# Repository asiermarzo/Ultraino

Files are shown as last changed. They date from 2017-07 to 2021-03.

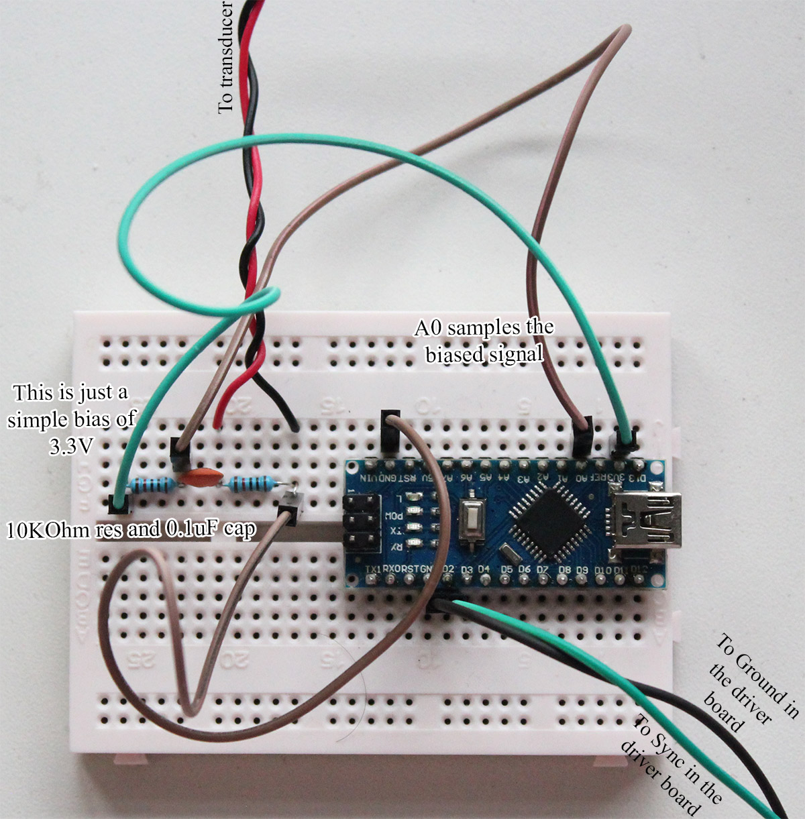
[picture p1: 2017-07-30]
Arduino phase detector/schematics.jpg

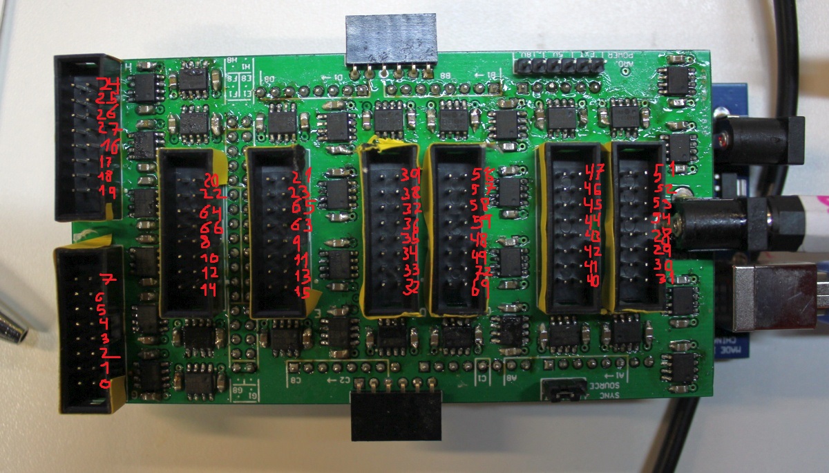
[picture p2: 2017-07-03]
DriverBoards/ArduinoMega64/driver board/ArduinoMEGA64 pin layout.JPG

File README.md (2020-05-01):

# Ultraino
Acoustic Field simulation for phased-array controllers. The content of the folders is as follows:
- AcousticField3D. The simulator that runs on the PC and can control the driver boards
- Arduino MEGA 64 driver board code. Source code that goes in the Arduino Mega 64-channel driver board.
- DriverNano16. Source code for making an Arduino Nano a 16-channel driver board.
- Arduino phase detector. Code that goes in an Arduino Nano to serve as a tool to assign the channels.
- arrays. Bases for example arrays.
- driver board. BOM and PCB files for the driver board.

# How to Run the Software
* Download the source as a zip file or checkout the repository.

* Be sure that you have installed JDK 11 https://www.oracle.com/java/technologies/javase-jdk11-downloads.html
* Install Netbeans Integrated Development Environment (you can also use Eclipse if you want). The Java SE pack is enough https://netbeans.org/downloads/

* Import the Source code in Netbeans. Run Netbeans, File->Open Project, Select the folder with the sourcecode.
* Click Run. You can click Run->Run project. It will take some time the first time since it needs to compile the sourcecode.

# Install Arduino Software
* Install the Arduino IDE https://www.arduino.cc/en/Main/Software
* Run the Arduino IDE and connect the Arduino Board to your computer.
* In Tools->Board select Arduino/Genuino Mega or Mega 2560. In Tools->Ports select the port for your Arduino. You may need to install the drivers for your Arduino Board (specially if it is not a branded one). For the chip CH340 http://sparks.gogo.co.nz/ch340.html
* In the public interface of Program Files (x86)\Arduino\hardware\arduino\avr\cores\arduino\HardwareSerial.h
add the following inline functions
inline bool _dataAvailable() {return _rx_buffer_head != _rx_buffer_tail; }
inline byte _peekData() { return _rx_buffer[_rx_buffer_tail]; }
inline void _discardByte() { _rx_buffer_tail = (rx_buffer_index_t)(_rx_buffer_tail + 1) % SERIAL_RX_BUFFER_SIZE; } 
* Click the Icon for Upload

# Install the Channel detector (tiny device used to assign channels semiautomatically)
* There is a schematic in the folder
* Install the software in Arduino Nano

# How to Assemble and example Applications
Paper: http://ieeexplore.ieee.org/document/8094247/
Instructables: https://www.instructables.com/id/Ultrasonic-array/
Video: https://youtu.be/h0Mh0bIv9Fk

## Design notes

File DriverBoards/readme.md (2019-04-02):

# Driver Boards

These are the files required to build the electronics.

## SonicSurface-256
This is a 256 channel board based on the Intel Cycloine IV FPGA. It has integrated ultrasonic transducers and a phase resolution of pi/16.

## ArduinoMega-64
This is a 64 channel board based on the Arduino Mega. It has a phase resolution of pi/5

# Links to papers & instructables

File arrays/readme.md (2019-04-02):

# Files for building the ultrasonic arrays

## 3D printing files (.stl)
These are provided as stl files which can be opened by probably all 3D printer software.

## Laser cutting files (.ai)
These are provided in Adobe Illustrator format (.ai). Inkscape is recommneded to open these or Adobe Illustrator CS2 is now avaialble as free software although its very old.

## Simulation Files (.xml.gz)
The simulation files are gun-zipped xml files and have the extension .xml.gz - they are used in the Acoustic Field Simulator software which is also in this repository. 

# Parts List
* 20-core ribbon cable [from UK Farnell](http://uk.farnell.com/3m/3302-20/ribbon-cable-20core-28awg-per/dp/1207420)
* 3-way pcb connector
  * uk rs-components 506-7014
* female molex connector
  * uk rs-components 323-7873
* 40khz 1cm diameter transducers
 * MURATA: uk rs-components 237-0799
* The murata transducers are a little bit pricey so here are some alternatives:
  * Manorshi Black 10mm - 0.34$ - MSO-P1040H07T [from alibaba](https://manorshi.en.alibaba.com)
  * Ningbo Black 10mm - 0.38$ - 'dog repeller' [from alibaba](FBULS1007P-T https://bestgroup.en.alibaba.com/product/987365133-800848321/dog_repeller_ultrasonic_transducer_40khz_black_plastic_ultrasonic_sensor_ultrasonic_depth_sensor.html)

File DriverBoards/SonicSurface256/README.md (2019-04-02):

# SonicSurface-256

The build instructions will be added here once we get around to it.

## Build Of Materials (BOM)

## Phase Calibration & board rotation

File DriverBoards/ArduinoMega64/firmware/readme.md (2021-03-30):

DriverMEGA is the normal code. It can upload up to 32 patterns and then a script is sent that indicates how many periods each pattern should be played.
DriverMEGAAnim is designed to upload 32 patterns at the same time and then send only one byte for the desired pattern
DriverMEGAStatic is designed for operating without a computer since the 32 patterns are predefined and it is possible to cycle through them by external buttons. These patterns can be generated with the simulator.

Please do not forget to add in the public interface of HardwareSerial the following inlines: 

inline bool _dataAvailable() {return _rx_buffer_head != _rx_buffer_tail; }
inline byte _peekData() { return _rx_buffer[_rx_buffer_tail]; }
inline void _discardByte() { _rx_buffer_tail = (rx_buffer_index_t)(_rx_buffer_tail + 1) % SERIAL_RX_BUFFER_SIZE; }

They are located at Program Files (x86)\Arduino\hardware\arduino\avr\cores\arduino\HardwareSerial.h
For MAC the path may be "HD -> Applications -> Arduino -> Contents -> Java -> hardware -> arduino -> avr -> cores -> arduino"

Just after the line "public:" is fine.

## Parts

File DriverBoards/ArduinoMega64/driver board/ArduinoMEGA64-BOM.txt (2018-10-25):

62mm by 115mm 
4 layers

32x TC4427A SMD / or MIC4127 for more voltage
	uk rs-components 889-5409
32x caps ceramic SMD 0805 0.1uf above 25V
	uk rs-components 264-4416
32x caps ceramic SMD 0805 4.7uf above 25V
	uk rs-components 820-2778
8x MOLEX male 16way connectors
	http://uk.farnell.com/amphenol/t821116a1s100ceu/header-vertical-2-54mm-16way/dp/2215308
	http://uk.farnell.com/molex/70246-1604/header-shrouded-16way/dp/1392536
1x DC barrel
	http://amzn.eu/7HL7QDk
Headers pins
	http://amzn.eu/bA4vE4o
90deg angle pins female and female 6-way
	http://amzn.eu/a4pMjJ7
jumper
	http://amzn.eu/7xdVyIM

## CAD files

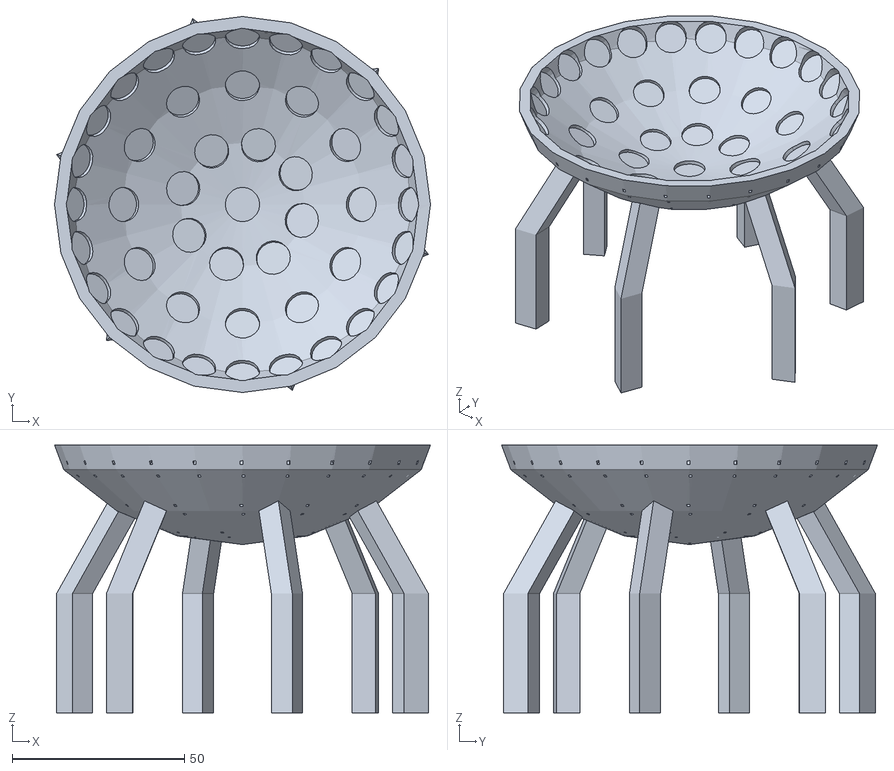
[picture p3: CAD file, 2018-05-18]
arrays/sphericalCap48.STL
109.3 x 109.3 x 77.9

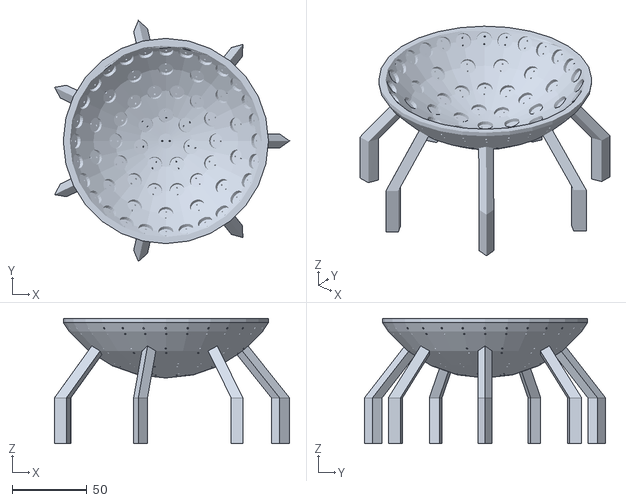
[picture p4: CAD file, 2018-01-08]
arrays/sphericalCap64.STL
157.7 x 161.7 x 83.9

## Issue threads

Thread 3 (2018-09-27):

asiermarzo/Ultraino #3: DriverNano16

vrossbach, 2018-09-27:
I am trying to upload the code for DriverNano16 in the Arduino Uno and this error messages appear:

'class HardwareSerial' has no member named '_dataAvailable'
'class HardwareSerial' has no member named '_peekData'

I tried to put the functions Serial.available() and Serial.peek() but then there is a error to compile to Arduino Uno board. Is there a different code for Arduino Uno or the code was written in another version?

asiermarzo, 2018-09-27:
Try the instructions on https://github.com/asiermarzo/Ultraino/blob/master/Arduino%20MEGA%2064%20driver%20board%20code/readme.txt

Best

vrossbach, 2018-09-27:
Hi, 

now I got, I had not pasted the code in the correct public position.

Thank you!

closed 2019-03-29 by asiermarzo

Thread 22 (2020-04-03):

asiermarzo/Ultraino #22: Noise on signal when doing semi-manual pin assignment, software frozen

littlejacinthe, 2020-04-03:
Hello, 

When doing the semi-manual pin assignment following the steps of your video, we noticed that :
- The Ultraino software stops working at : 
Transducer Assignment menu > Connect (Arduino Nano is connected correctly) > Start > Check.  Once we click on the 'check' command there is no output when it should show numbers for Selected, Pin, Amplitude, Phase. After that the software is completely frozen and we have to restart it. 
It probably is because the software does not detect the signal coming from the transducers correctly, as when we checked it with the oscilloscope : 
- There is noise provided by the transducer used to check the signal when it's connected to wires. We tried different wires but there was always noise, which doesn't happen when the transducer is directly connected to the probe of the oscilloscope.

We used all materials recommended as well the codes provided during this experiment. 
Our driver is an Arduino MEGA, and we are working on an 8x8 flat array. 
You can see how we proceeded on [this video](https://youtu.be/fm1WUwtMGUc). It shows more precisely the problem that we're having. 

Would you have any idea why is this happening and how to solve the problem ?

Thank you

asiermarzo, 2020-04-08:
Hi,
Very good work with the video and with the hardware. Ultraino started as research and still needs a lot of brushing up.

a) Have you installed the phase-detector sketch in the arduino that is used to detect the pins?
b) when you connect the driverboard and the phase-detector have you identified which COM port is which?
c) be sure to connect the main program to the board and the connect of the assignments to the phase detector.

In any case, I will try to add more debug messages and avoid the software from hanging.

Best,
Asier.

littlejacinthe, 2020-04-10:
Hello, 

a) we installed the phase-detector sketch using the same materials 
[image]
b) and c) We made the mistake of connecting the wrong ports before but corrected it and then this noise problem came up. 

We are going to order brand new materials for the phase detector as the ones we've been using are not and there might be a default there. 

Thanks for your reply !

littlejacinthe, 2020-04-16:
Hello, 

After changing the hardware of the arduino phase detector, we still got the same error. 

I noticed when connecting the Arduino Nano that we have to use the old bootloader for ATMega 328P otherwise it doesn't upload the code. It seems like the bootloader was updated in 2018. Could it be that you used the new bootloader ? 

Also on line 34 of the phase detector code, the line should print the samples array. When the board is connected to the simulation software it says the port is busy, and when the board is not connected to the simulation software (with only the Mega board sending the signal to the transducers) the monitor is empty. Is that normal ?

Thanks

asiermarzo, 2020-09-13:
It is not possible to have the phase detector working and the serial monitor connected to it. Have you selected the transducers in the order that you want them tested and then pressed the button Order? Otherwise, all of them may have order 0 and cause problems. Best. I know the phase assignment works like shit, I need to brush it up asap.

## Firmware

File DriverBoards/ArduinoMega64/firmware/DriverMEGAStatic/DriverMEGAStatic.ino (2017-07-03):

#include <avr/sleep.h>
#include <avr/power.h>

#define N_PATTERNS 8

#define N_PORTS 10
#define N_DIVS 10

//ports A C L B K F H D G J

#define COMMAND_SWITCH 0b00000000
#define COMMAND_DURATION 0b00110000
#define MASK_DURATION 0b00111111
#define COMMAND_COMMITDURATIONS 0b00010000

#define WAIT(a) __asm__ __volatile__ ("nop")
#define OUTPUT_WAVE(pointer, d)  PORTA = pointer[d*N_PORTS + 0]; PORTC = pointer[d*N_PORTS + 1]; PORTL = pointer[d*N_PORTS + 2]; PORTB = pointer[d*N_PORTS + 3]; PORTK = pointer[d*N_PORTS + 4]; PORTF = pointer[d*N_PORTS + 5]; PORTH = pointer[d*N_PORTS + 6];  PORTD = pointer[d*N_PORTS + 7]; PORTG = pointer[d*N_PORTS + 8]; PORTJ = pointer[d*N_PORTS + 9]

static byte bufferA[N_PATTERNS * N_DIVS * N_PORTS];
static byte bufferB[N_PATTERNS * N_DIVS * N_PORTS];

static byte animation[100] = {0x38,0xa8,0xb4,0x3,0x2,0xfc,0x43,0xc,0x4,0x0,0x3d,0xaa,0xac,0x3,0x2,0xfc,0x43,0xc,0x7,0x0,0x5,0x3,0x8,0xe4,0x38,0x6d,0x19,0xb,0x3,0x1,0x7,0x43,0xa,0xe4,0x38,0x6d,0x19,0x8b,0x3,0x1,0x7,0x43,0xa,0xe4,0x38,0x1,0x18,0x83,0x3,0x1,0x7,0x57,0x4b,0xfc,0x3d,0x3,0x38,0x83,0x23,0x1,0x2,0x55,0x53,0xfc,0x3d,0x3,0x38,0x83,0x20,0x1,0x3a,0xfc,0xf7,0x1b,0x7,0x92,0x62,0x84,0x24,0x0,0x38,0xbc,0xf5,0x1b,0x7,0x92,0x62,0x4,0x24,0x0,0x38,0xbc,0xf5,0x1b,0x7,0xfe,0x63,0xc,0x24,0x0};

void setup()
{
  //set as output ports A C L B K F H D G J
  DDRA = DDRC = DDRL = DDRB = DDRK = DDRF = DDRH = DDRD = DDRG = DDRJ = 0xFF;
  //low signal on all of them
  PORTA = PORTC = PORTL = PORTB = PORTK = PORTF = PORTH = PORTD = PORTG = PORTJ = 0x00;

  //clear the buffers
  for (int i = 0; i < (N_PATTERNS * N_DIVS * N_PORTS); ++i) {
    bufferA[i] = bufferB[i] = 0;
  }

//initial pattern
/*
  for (int i = 0; i < (N_PORTS*N_DIVS/2); ++i){
     bufferA[i] = 0xFF;
     //bufferA[i] = bufferB[i] = animation[i];
  }
  */
 
   for (int i = 0; i < 100; ++i){
      bufferA[i] =  animation[i];
   }

 for (int i = 0; i < 100; ++i){
       bufferB[i] =  animation[i];
   }

  //a patterns of 01s at pin 22, for debuging and adjusting times
 /*
  for(int i = 0; i < N_DIVS; ++i){
    if (i % 2 == 0){
      bufferA[i * N_PORTS] |= 0b00001000;
    }else{
      bufferA[i * N_PORTS] &= 0b11110111;
    }
  }
 */
  
  // generate a sync signal of 40khz in pin 2
  pinMode (2, OUTPUT);
  noInterrupts();           // disable all interrupts
  TCCR3A = bit (WGM10) | bit (WGM11) | bit (COM1B1); // fast PWM, clear OC1B on compare
  TCCR3B = bit (WGM12) | bit (WGM13) | bit (CS10);   // fast PWM, no prescaler
  OCR3A =  (F_CPU / 40000L) - 5; //should only be -1 but fine tunning with the scope determined that -5 gave 40kHz almost exactly
  OCR3B = (F_CPU / 40000L) / 2;
  interrupts();             // enable all interrupts

  //sync in signal at pin 3
  pinMode(3, INPUT_PULLUP); //please connect pin3 to pin 2


  // disable everything that we do not need
  ADCSRA = 0;  // ADC
  power_adc_disable ();
  power_spi_disable();
  power_twi_disable();
  power_timer0_disable();
  power_usart1_disable();
  power_usart2_disable();
  power_usart3_disable();
  //power_usart0_disable();

  Serial.begin(115200);

  byte bReceived = 0;
  bool byteReady = false;
  bool isSwitch = false;
  bool isPatternForMe = false;
  bool isDuration = false;
  bool isCommitDurations = false;
  byte nextMsg = 0;
  int writtingIndex = 0;

  bool emittingA = true;
  byte* emittingPointerH = & bufferA[0];
  byte* emittingPointerL = & bufferA[N_PORTS * N_DIVS / 2];
  byte* emittingPointerZeroH = & bufferA[0];
  byte* emittingPointerZeroL = & bufferA[N_PORTS * N_DIVS / 2];
  byte* readingPointerH = & bufferB[0];
  byte* readingPointerL = & bufferB[N_PORTS * N_DIVS / 2];

  byte durations[N_PATTERNS];
  byte durationsBuffer[N_PATTERNS];
  for(int i = 0; i < N_PATTERNS; ++i){
    durations[i] = durationsBuffer[i] = 0;
  }
  durations[0] = durationsBuffer[0] = 1;

  byte currentPattern = 0;
  byte currentPeriods = 0;
  byte durationsPointer = 0;
  byte currentDuration = 0;
  bool patternComplete = false;
  bool lastPattern = false;
  byte nextPattern = 0;
  byte nextDuration = 0;
  bool returnToFirstPattern = false;
LOOP:
  while (PINE & 0b00100000); //wait for pin 3 (E5 Sync In) to go low

  OUTPUT_WAVE(emittingPointerH, 0); byteReady = Serial._dataAvailable(); 
  OUTPUT_WAVE(emittingPointerH, 1); bReceived = Serial._peekData(); 
  OUTPUT_WAVE(emittingPointerH, 2); isSwitch = bReceived == COMMAND_SWITCH; isCommitDurations = bReceived == COMMAND_COMMITDURATIONS; 
  OUTPUT_WAVE(emittingPointerH, 3); isPatternForMe = (bReceived & 0b00001111) == 1; ++currentPeriods; 
  OUTPUT_WAVE(emittingPointerH, 4); nextMsg =  bReceived - 1; 
  OUTPUT_WAVE(emittingPointerL, 0); isDuration = (bReceived & MASK_DURATION) == COMMAND_DURATION; nextPattern = currentPattern + 1;
  OUTPUT_WAVE(emittingPointerL, 1); nextDuration = durations[nextPattern]; 
  OUTPUT_WAVE(emittingPointerL, 2); patternComplete = (currentPeriods == durations[currentPattern]); 
  OUTPUT_WAVE(emittingPointerL, 3); lastPattern = (currentPattern+1 == N_PATTERNS); returnToFirstPattern = nextDuration == 0;
  OUTPUT_WAVE(emittingPointerL, 4); 
  
if (patternComplete){
  currentPeriods = 0;
  ++currentPattern;
  if (lastPattern  || returnToFirstPattern){
    currentPattern = 0;
    emittingPointerH = emittingPointerZeroH;
    emittingPointerL = emittingPointerZeroL;
  }else{
    emittingPointerH += (N_DIVS * N_PORTS);
    emittingPointerL += (N_DIVS * N_PORTS);
  } 
}
  
  if (byteReady) {
    if ( isSwitch ) {
      Serial.write( COMMAND_SWITCH );
      emittingA = !emittingA;
      if (emittingA) {
        emittingPointerH = & bufferA[0];
        emittingPointerL = & bufferA[N_PORTS * N_DIVS / 2];
        readingPointerH = & bufferB[0];
        readingPointerL = & bufferB[N_PORTS * N_DIVS / 2];
      } else {
        emittingPointerH = & bufferB[0];
        emittingPointerL = & bufferB[N_PORTS * N_DIVS / 2];
        readingPointerH = & bufferA[0];
        readingPointerL = & bufferA[N_PORTS * N_DIVS / 2];
      }
      emittingPointerZeroH = emittingPointerH;
      emittingPointerZeroL = emittingPointerL;
      
      writtingIndex = 0;
      durationsPointer = 0;
    } else if ( isPatternForMe ) {
        if (writtingIndex % 2 == 0) {
          readingPointerH[writtingIndex / 2] = bReceived & 0xF0;
        } else {
          readingPointerH[writtingIndex / 2] |= (bReceived >> 4);
        }
        ++writtingIndex;
    } else if (isDuration){
        Serial.write( bReceived );
        if (durationsPointer % 4 == 0) {
          durationsBuffer[durationsPointer / 4] = bReceived & 0b11000000;
        } else {
          durationsBuffer[durationsPointer / 4] |= (bReceived & 0b11000000) >> (durationsPointer % 4 * 2);
        }
        ++durationsPointer;
    }else if (isCommitDurations){
      Serial.write( bReceived );
      for(int i = 0; i<N_PATTERNS; ++i){
        durations[i] = durationsBuffer[i];
      }
      durationsPointer = 0;
    } else {
      Serial.write( nextMsg );
    }
    Serial._discardByte();
  }

  goto LOOP;

}

void loop() {}

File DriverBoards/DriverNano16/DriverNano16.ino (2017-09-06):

#include <avr/sleep.h>
#include <avr/power.h>

#define N_PORTS 2
#define N_DIVS 16

#define COMMAND_SWITCH 0b00000000
#define COMMAND_RESET 0b00010000

#define WAIT_A(a) __asm__ __volatile__ ("nop"); __asm__ __volatile__ ("nop"); __asm__ __volatile__ ("nop");  __asm__ __volatile__ ("nop"); __asm__ __volatile__ ("nop");__asm__ __volatile__ ("nop"); __asm__ __volatile__ ("nop");__asm__ __volatile__ ("nop"); __asm__ __volatile__ ("nop");  __asm__ __volatile__ ("nop"); __asm__ __volatile__ ("nop");__asm__ __volatile__ ("nop");  __asm__ __volatile__ ("nop"); __asm__ __volatile__ ("nop"); __asm__ __volatile__ ("nop");__asm__ __volatile__ ("nop");  __asm__ __volatile__ ("nop"); __asm__ __volatile__ ("nop");  __asm__ __volatile__ ("nop"); __asm__ __volatile__ ("nop")
#define WAIT_B(a) __asm__ __volatile__ ("nop"); __asm__ __volatile__ ("nop"); __asm__ __volatile__ ("nop");  __asm__ __volatile__ ("nop"); __asm__ __volatile__ ("nop");__asm__ __volatile__ ("nop"); __asm__ __volatile__ ("nop");__asm__ __volatile__ ("nop"); __asm__ __volatile__ ("nop"); __asm__ __volatile__ ("nop"); __asm__ __volatile__ ("nop"); __asm__ __volatile__ ("nop"); __asm__ __volatile__ ("nop"); __asm__ __volatile__ ("nop"); __asm__ __volatile__ ("nop"); __asm__ __volatile__ ("nop")
#define WAIT_C(a) __asm__ __volatile__ ("nop"); __asm__ __volatile__ ("nop"); __asm__ __volatile__ ("nop");  __asm__ __volatile__ ("nop"); __asm__ __volatile__ ("nop");  __asm__ __volatile__ ("nop");  __asm__ __volatile__ ("nop"); __asm__ __volatile__ ("nop");  __asm__ __volatile__ ("nop"); __asm__ __volatile__ ("nop");  __asm__ __volatile__ ("nop");  __asm__ __volatile__ ("nop")


#define OUTPUT_WAVE(pointer, d)  PORTC = pointer[d*N_PORTS + 0]; PORTD = pointer[d*N_PORTS + 1]

static byte bufferA[N_DIVS * N_PORTS];
static byte bufferB[N_DIVS * N_PORTS];

void setup()
{
  //initialize the buffers
  for (int i = 0; i < (N_PORTS*N_DIVS); ++i){
    bufferA[i] = bufferB[0] = 0;
  }

  for (int i = 0; i < (N_PORTS*N_DIVS/2); ++i){
     bufferA[i] = 0b11111111;
  }
  
 /*
  //only for calibrating WAITs
  for(int i = 0; i < N_DIVS; ++i){
    if (i % 2 == 0){
      bufferA[i * N_PORTS] |= 0b00001000;
    }else{
      bufferA[i * N_PORTS] &= 0b11110111;
    }
  }
  */

  // generate a sync signal of 40khz in pin 10
  pinMode (10, OUTPUT);
  noInterrupts();           // disable all interrupts
  TCCR1A = bit (WGM10) | bit (WGM11) | bit (COM1B1); // fast PWM, clear OC1B on compare
  TCCR1B = bit (WGM12) | bit (WGM13) | bit (CS10);   // fast PWM, no prescaler
  OCR1A =  (F_CPU / 40000L) - 1;
  OCR1B = (F_CPU / 40000L) / 2;
  interrupts();             // enable all interrupts

  //sync in signal at pin 3
  pinMode(11, INPUT_PULLUP); //please connect pin 10 to pin 11
  

  // disable everything that we do not need 
  ADCSRA = 0;  // ADC
  power_adc_disable ();
  power_spi_disable();
  power_twi_disable();
  power_timer0_disable();
  //power_usart0_disable();

  Serial.begin(115200);

   DDRC = 0b00111111;
   DDRD = 0b11111100; 
   PORTC = 0b00000000; 
   PORTD = 0b00000000; 
   
 byte bReceived = 0;
 bool byteRead = false;
 bool isSwitch = false;
 bool isReset = false;
 bool isForMe = false;
 byte nextMsg = 0;
 int writtingIndex = 0;

 byte* emittingPointer = & bufferA[0];
 byte* readingPointer = & bufferB[0];

  LOOP:
    while(PINB & 0b00001000); //wait for pin 11 (B3) to go low 
    
    OUTPUT_WAVE(emittingPointer, 0); byteRead = Serial._dataAvailable(); WAIT_C();
    OUTPUT_WAVE(emittingPointer, 1); bReceived = Serial._peekData(); WAIT_C();
    OUTPUT_WAVE(emittingPointer, 2); isSwitch = bReceived == COMMAND_SWITCH; WAIT_B();
    OUTPUT_WAVE(emittingPointer, 3); isReset = bReceived == COMMAND_RESET; WAIT_B();
    OUTPUT_WAVE(emittingPointer, 4); isForMe = (bReceived & 0b00001111) == 1; WAIT_B(); 
    OUTPUT_WAVE(emittingPointer, 5); nextMsg =  bReceived - 1; WAIT_B();
    OUTPUT_WAVE(emittingPointer, 6); WAIT_A();
    OUTPUT_WAVE(emittingPointer, 7); WAIT_A();
    OUTPUT_WAVE(emittingPointer, 8); WAIT_A();
    OUTPUT_WAVE(emittingPointer, 9); WAIT_A();
    OUTPUT_WAVE(emittingPointer, 10); WAIT_A();
    OUTPUT_WAVE(emittingPointer, 11); WAIT_A();
    OUTPUT_WAVE(emittingPointer, 12); WAIT_A();
    OUTPUT_WAVE(emittingPointer, 13); WAIT_A();
    OUTPUT_WAVE(emittingPointer, 14); WAIT_A();
    OUTPUT_WAVE(emittingPointer, 15);

    if (byteRead){
        if ( isSwitch ){
          Serial.write( COMMAND_SWITCH );
          byte* tmpPointer = emittingPointer;
          emittingPointer = readingPointer;
          readingPointer = tmpPointer;
          
          writtingIndex = 0;
        }else if ( isReset ){
          Serial.write( COMMAND_RESET );
          writtingIndex = 0;
        }else if ( isForMe ){
          if (writtingIndex % 2 == 0){
            readingPointer[writtingIndex / 2] = bReceived & 0xF0;
          }else{
            readingPointer[writtingIndex / 2] |= (bReceived >> 4);
          }
          ++writtingIndex;
        }else{
          Serial.write( nextMsg );
        }
        Serial.read();
    }
    
  goto LOOP;
  
}

void loop(){}

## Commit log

2017-11-15 Update BOM and specs driver board ArduinoMEGA64.txt
2018-01-08 corrected the scale of the bowl.stl
    [spherical cap.STL]
2019-04-02 restructued folders
    [ArduinoMEGA64 pin assignment and phase compensation.xlsx]
2020-01-31 When an array is imported from a csv the simulation size and camera is adjusted afterwards.
2021-01-05 Added precompiled version for DriverMEGA since it only compiles fine with Arduino IDE 1.6
2021-01-08 Pressing control or meta to select multiple objects now works The phase assigner does not block if not samples are received
2021-04-01 Corrected the push-pull driving of the boards.
2021-04-19 Added an options to add the current key frame N times
2021-04-29 Add files via upload
    Added the simulation file for SonicSurface single board 10mm emitters
2021-04-29 SonicSurface sim file now has pin numbering
2023-05-26 flat8x8 has sequential pin numbering
2025-04-30 Added tube arrangement
2025-05-06 Iso surface cut volume
    When the volume cuts the iso-surface it sets the normal to the volume cube (flat) and swaps the color sign.
2025-05-08 outline cut to vol renderer
    The intersection of the isosurface with the cube volume is stripped with grey
